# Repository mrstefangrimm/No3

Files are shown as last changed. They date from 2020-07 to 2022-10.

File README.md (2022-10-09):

# Lung Motion X-Ray Imaging Phantom
No3 (working title) is a motion phantom with 3 motion axes which are controlled independently for both linear and rotary motion.

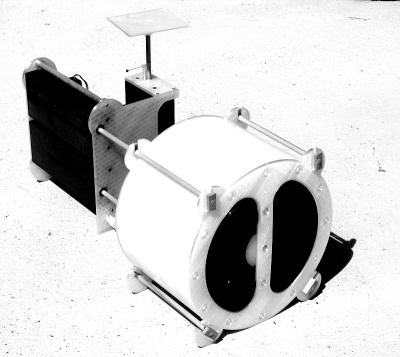
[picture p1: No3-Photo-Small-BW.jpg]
No3 Motion Phantom


A [video on youtube](https://youtu.be/cEjuUass-fE) shows how the phantom works.

## Project History
The project was realized in 2020.

## Construction

A detailed description how to build this phantom was published on *instructables.com* but removed because of a possible copyright infringement.

## Manufacturing Tool Chain

Software | License 
---- | -------
SketchUp | SketchUp Shop 
Ultimaker Cura | GPL

## License


This work is licensed under the Creative Commons Attribution-ShareAlike 4.0 International License. To view a copy of this license, visit http://creativecommons.org/licenses/by-sa/4.0/ or send a letter to Creative Commons, PO Box 1866, Mountain View, CA 94042, USA.

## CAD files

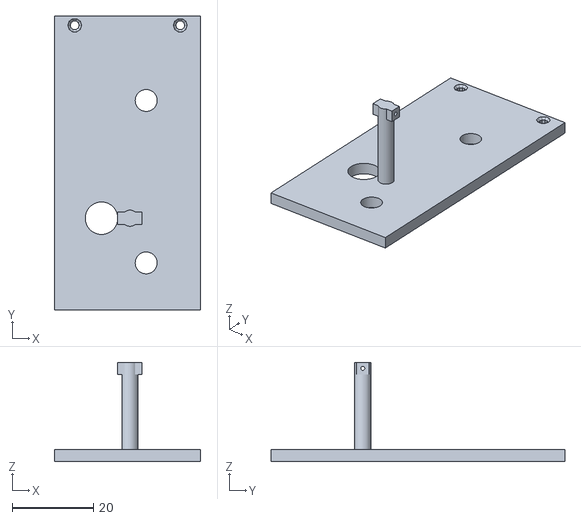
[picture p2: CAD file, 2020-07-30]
MechanicalDesign/Sketchup/Export/No3-GatingTopLeft.stl
36.0 x 72.4 x 24.5

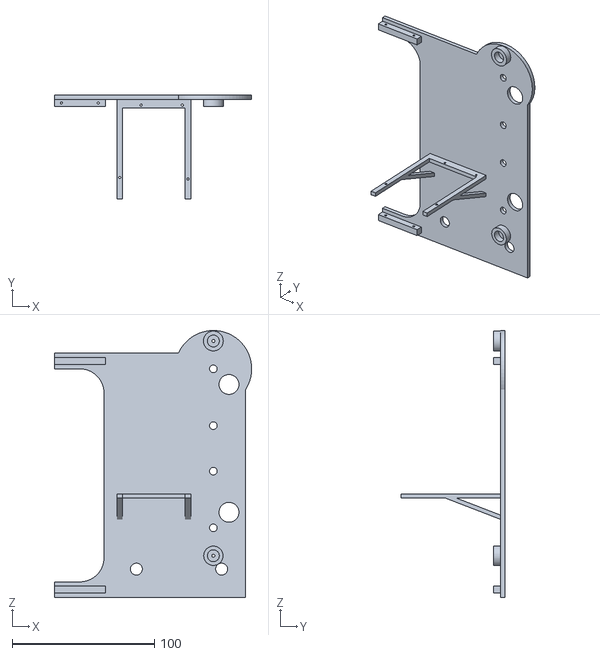
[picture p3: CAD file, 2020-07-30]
MechanicalDesign/Sketchup/Export/No3-Front.stl
139.0 x 73.0 x 188.0

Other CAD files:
MechanicalDesign/Sketchup/No3-Back.skp
MechanicalDesign/Sketchup/No3-CPUDistanceRing.skp
MechanicalDesign/Sketchup/No3-ChestBackPanel.skp
MechanicalDesign/Sketchup/No3-ChestForm.skp
MechanicalDesign/Sketchup/No3-ChestFormCover.skp
MechanicalDesign/Sketchup/No3-ChestFrontPanel.skp
MechanicalDesign/Sketchup/No3-ChestPositive.skp
MechanicalDesign/Sketchup/No3-Front.skp
MechanicalDesign/Sketchup/No3-GatingBottom.skp
MechanicalDesign/Sketchup/No3-GatingTop.skp
MechanicalDesign/Sketchup/No3-GatingTopLeft.skp
MechanicalDesign/Sketchup/No3-LungLeft.skp
MechanicalDesign/Sketchup/No3-LungLeftInsert.skp
MechanicalDesign/Sketchup/No3-LungLeftLowerCylinder.skp
MechanicalDesign/Sketchup/No3-LungLeftLowerCylinderInsert.skp
MechanicalDesign/Sketchup/No3-LungLeftUpperCylinder.skp
MechanicalDesign/Sketchup/No3-LungLeftUpperCylinderInsert.skp
MechanicalDesign/Sketchup/No3-LungRight.skp
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

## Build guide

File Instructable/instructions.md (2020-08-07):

# Lung Motion X-Ray Imaging Phantom

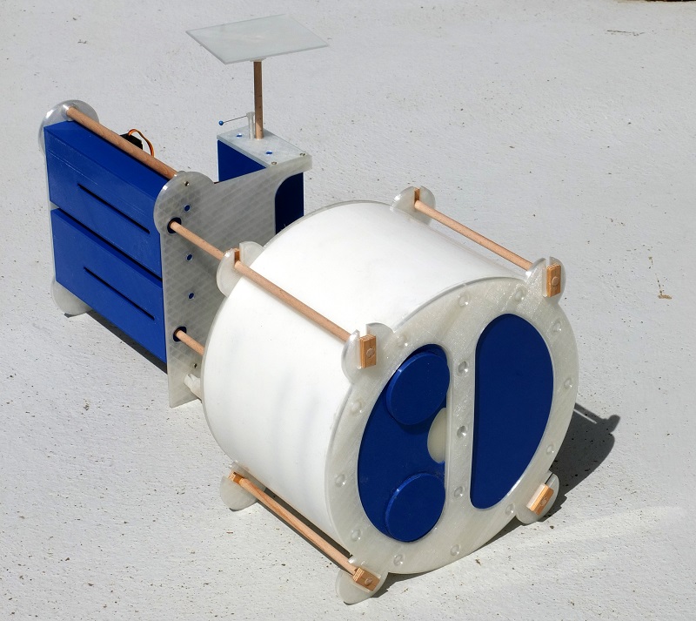
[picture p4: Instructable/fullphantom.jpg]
fullphantom


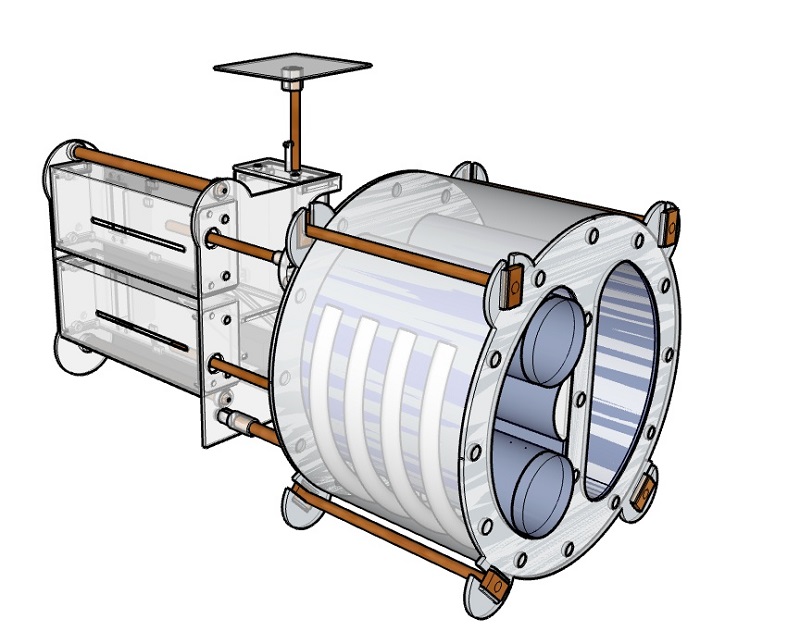
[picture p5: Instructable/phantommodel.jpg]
phantommodel


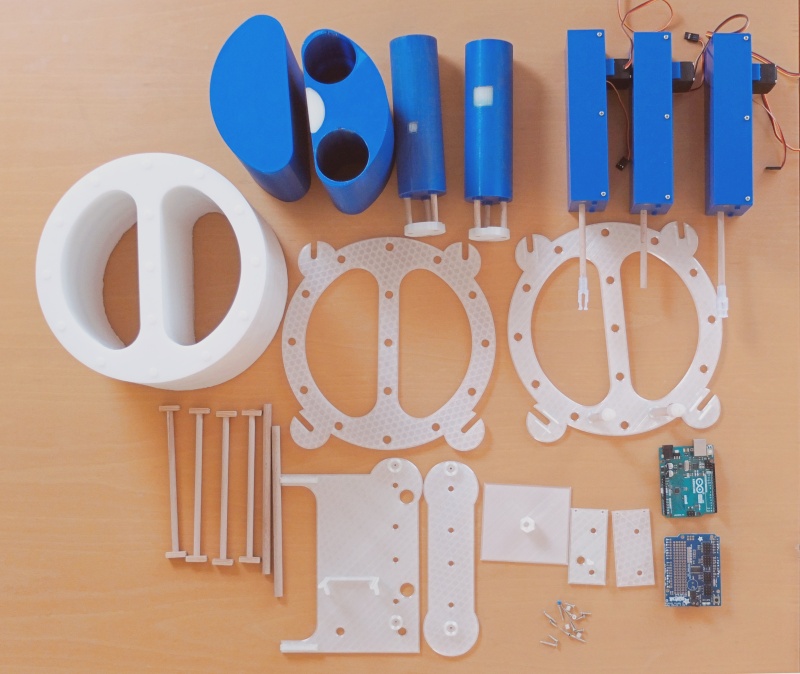
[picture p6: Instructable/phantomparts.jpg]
phantomparts


In the field of medical imaging, so called imaging phantoms are used  to evaluate, analyze, and tune the performance of various imaging  devices (Source: Wikipedia). This specially developed imaging  phantom simulates motion and deformation of a lung based on respiratory motion.

The idea for this phantom came when I studied breathing motion in a lung. The motion in the lung is not uniform. The lower part of the lung moves more sideways whereas the upper part of the lung moves up and down. To simulate this, a phantom is required that does not only simulate motion but also simulates deformation. One example that illustrates the motion in the lung: https://www.youtube.com/watch?v=kfcbAyLJHsI

On an X-Ray image, the material and the density define what is a  bone, a liver or a lung. Silicone for example is similar to human tissue whereas modelling plaster is similar to bone. The chest of this phantom is made of silicone, the cast-in rips are made of modelling plaster and the lungs are made of 3D printed PLA.

In the left lung,  there are two freely movable cylinders to simulate motion and deformation in the lung. In each cylinder there is a pocket and an object with a higher density than the density of the lung.

This short animation gives you an idea how this phantom would look like on X-Ray images. The two red arrows mark the two freely movable targets: https://youtu.be/TincNP1mlLw

To generate the motion, the phantom uses three [LnR-Actuators](https://www.instructables.com/id/Linear-and-Rotation-Actuator/), an Arduino micro controller and an Adafruit Servo Shield. The micro controller is  required because you cannot be in the room when you acquire X-Ray  images. The phantom can be either be remote controlled from a PC over an USB cable, or you can start one of the pre-programmed motion patterns and use the phantom stand-alone.

This phantom is suitable to evaluate and tune the performance of medical devices. A field of application could be the development of motion tracking and 4D reconstruction algorithms. With the used materials, imaging dosimetry should also be possible. 

The direct material costs are approximately USD 350.

### Supplies:

1 Arduino Uno

1 Adafruit 16-Channel Servo Shield

3 [LnR-Actuator](https://www.instructables.com/id/Linear-and-Rotation-Actuator/)

9 Screw M2 x l10

4 Screw M2 x l20

6 Wooden dowel d6 x l40 mm

4 Wooden dowel d6 x l150 mm

2 Wooden dowel d8 x l166 mm

2 Wooden dowel d8 x l120 mm

8 Wooden rectangular profile w10 x l20 x h4 mm with a hole d6 mm

1 Windows PC with Java 8 runtime and .NET Framework 4.6.2

1 3D Printer

1 Standing drill is of avail

750g PLA filament

750g PVA filament

3 kg of casting silicone

500g of modelling plaster

Legend: l:length, d:diameter, w: width, h:heigth

## Step 1: 3D Printed Parts

- PLA default, 20% infill: LMXIP-Back.stl, LMXIP-ChestBackPanel.stl, LMXIP-ChestFrontPanel.stl, LMXIP-CPUDistanceRing.stl, LMXIP-Front.stl, LMXIP-GatingBottom.stl, LMXIP-GatingTop.stl, Cmn-FrontClip.stl, Cmn-Flange.stl, Cmn-FlangeClip.stl, Cmn-GatingPlatform.stl

- PLA target, 90% infill: LMXIP-LungLeftInsert.stl, LungLeftLowerCylinderInsert.stl, LMXIP-LungLeftUpperCylinderInsert.stl

- PLA lung, 10% infill: LMXIP-LungLeft.stl, LMXIP-LungLeftLowerCylinder.stl, LMXIP-, LMXIP-LungLeftUpperCylinder.stl, LMXIP-LungRight.stl

- PVA form, 20% infill: LMXIP-ChestFormCover.stl, LMXIP-RipsForm.stl, LMXIP-SpineElementForm.stl, LMXIP-ChestForm.stl

## Step 2: Build the Skeleton

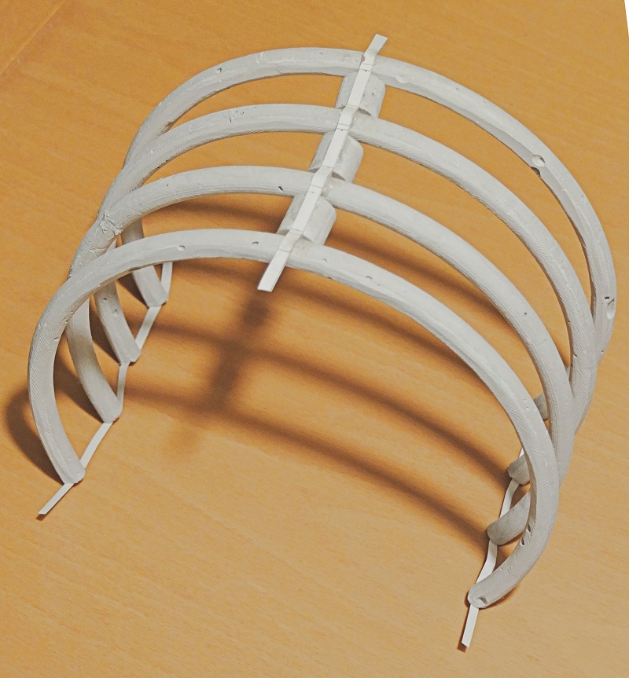
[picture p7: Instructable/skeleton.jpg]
skeleton


Mix some modeling plaster and fill the printed forms *LMXIP-RipsForm* and *LMXIP-SpineElementForm*. Wait until the plaster has dried; one day at least. Then wash off the PVA form. The plaster will not dissolve.

Use three small paper strips and glue the elements together. This is needed to insert the skeleton into the chest form.

## Step 3: Build the Phantom Body

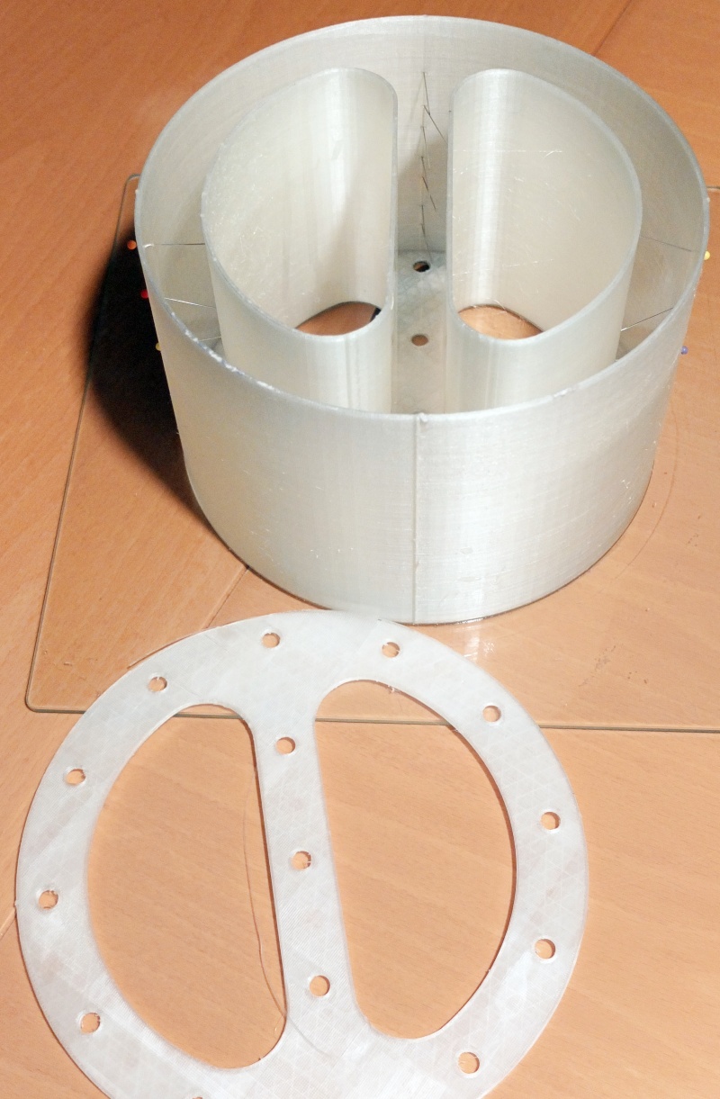
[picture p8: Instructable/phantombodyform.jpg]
phantombodyform


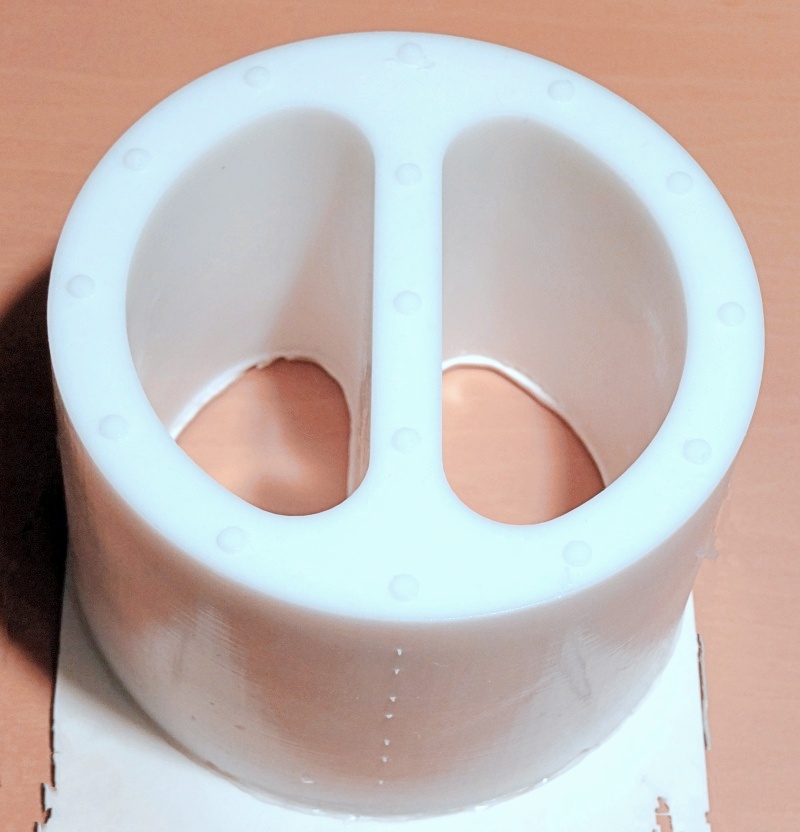
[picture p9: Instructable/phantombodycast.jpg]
phantombodycast


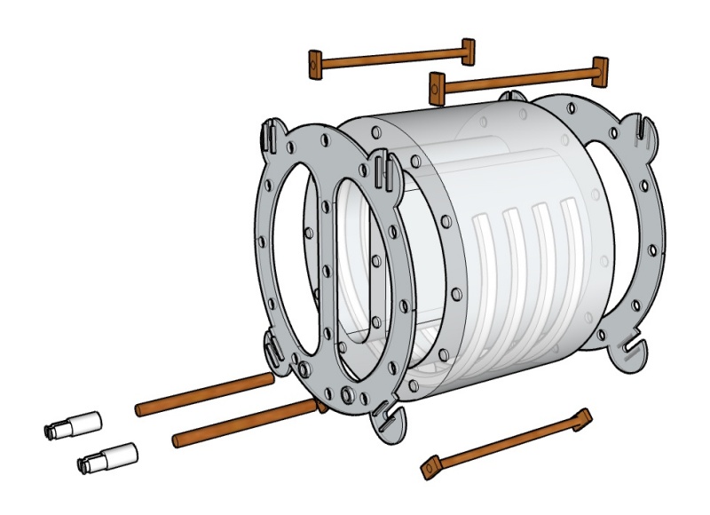
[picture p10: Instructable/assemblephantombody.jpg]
assemblephantombody


Insert the skeleton into the *LMXIP-ChestForm*. Use some pins as shown on the picture to hold the skeleton in place.

Mix the casting silicone and gentle cast it into the form. Add the *LMXIP-ChestFormCover* and wait until the silicone has hardened (read the data sheet from the manufacturer). Then wash off the PVA form.

Glue the handles (rectangular profile w10 x l20 x h4 mm) to the wooden dowels d6 x l150 mm.

Fixate the *LMXIP-ChestFrontPanel* and the *LMXIP-ChestBackPanel* with the created handles.

Insert two wooden dowels d8 x l110 mm into the holes in the front panel and attach a *Cmn-FrontClip.*

## Step 4: Add the Lungs

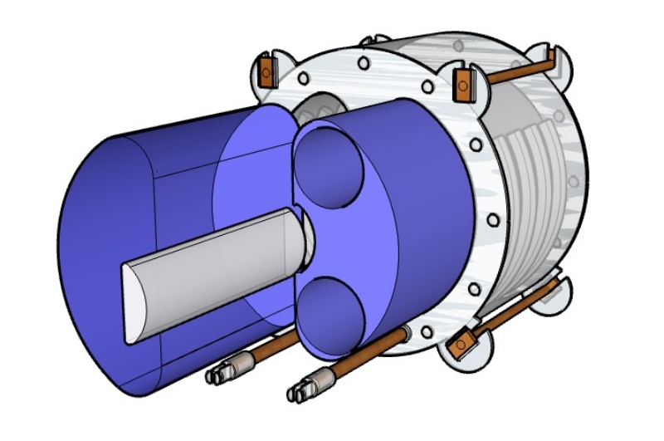
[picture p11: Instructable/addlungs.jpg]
addlungs


Glue the *LMXIP-LungLeftInsert* to the *LMXIP-LungLeft*. Gently push the *LMXIP-LungLeft* and the *LMXIP-LungRight* into the phantom.

## Step 5: Assemble the two Cylinders

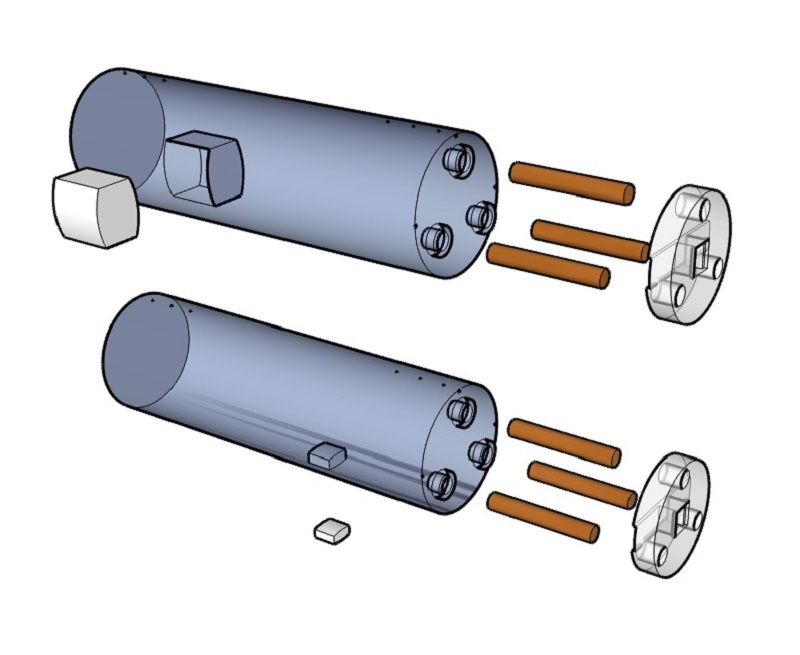
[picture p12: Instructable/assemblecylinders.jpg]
assemblecylinders


Insert the *LMXIP-LungLeftUpperCylinderInsert* into the *LMXIP-LungLeftUpperCylinder* and fixate it with a drop of glue. Insert three wooden dowels d6 x l40 mm into the holes in the front plane of the cylinder and attach a *Cmn-Flange*.

Insert the *LungLeftLowerCylinderInsert* into the *LMXIP-LungLeftLowerCylinder* and fixate it with a drop of glue. Insert three wooden  dowels d6 x l40 mm into the holes in the front plane of the cylinder and attach a *Cmn-Flange*.

## Step 6: Assemble the Actuator

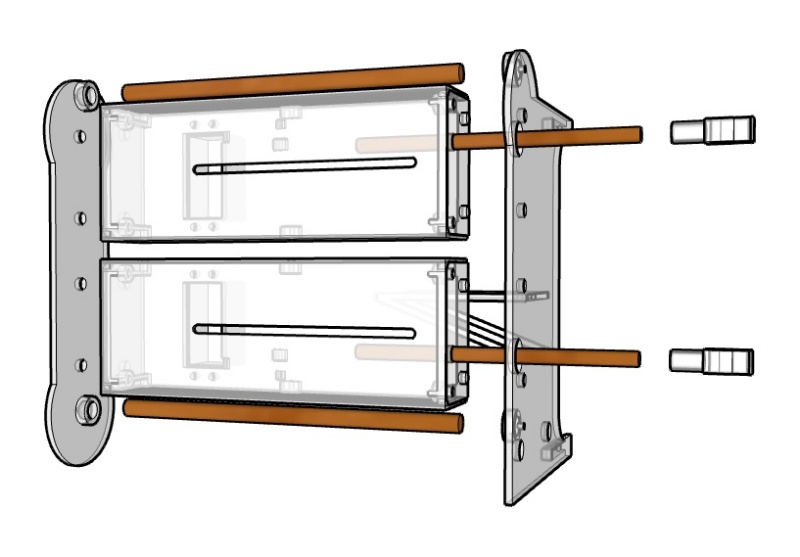
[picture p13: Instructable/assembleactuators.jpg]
assembleactuators


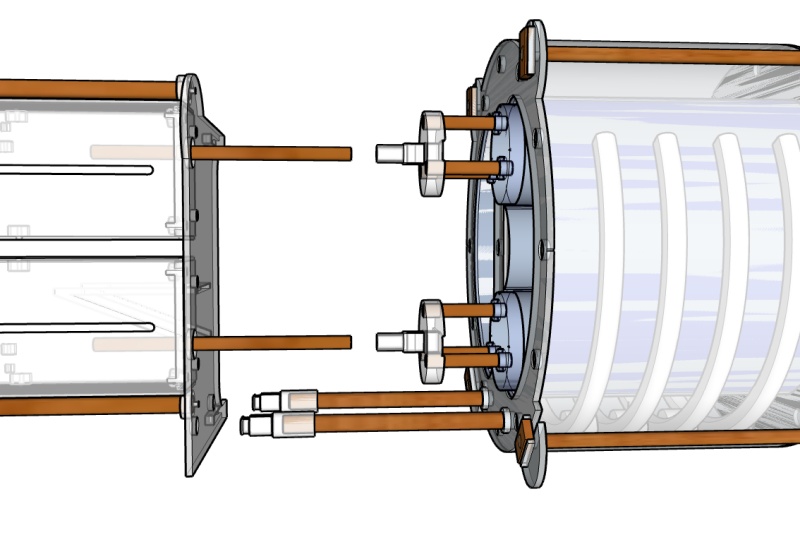
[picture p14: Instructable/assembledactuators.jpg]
assembledactuators


To build the actuator assembly, fixate two wooden dowels d8 x l166 mm to the *LMXIP-Back* with two screws M2 x l20 mm. Plug-in the two LnR-Actuators and add the *LMXIP-Front*. Add a *Cmn-FlangeClip* to each of the LnR-Actuator shafts but do not fixate it yet.

Plug-in the assembled phantom body into the actuator assembly. Connect the  flange-clip with the flange. Align the cylinders and then fixate the flange clips with some glue to the actuator shafts.

## Step 7: Add the Gating Platform

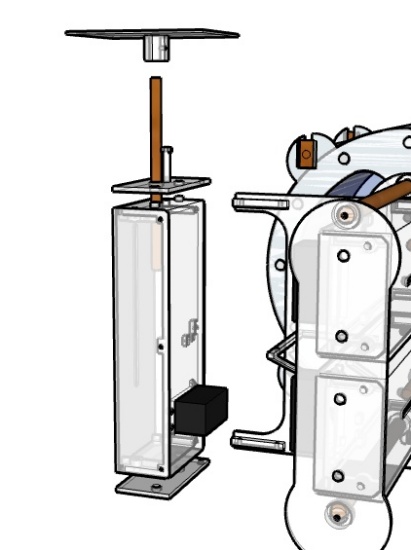
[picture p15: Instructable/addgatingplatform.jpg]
addgatingplatform


To build the Gating assembly, attach the *LMXIP-GatingBottom* to the *LMXIP-Front* with two screws M2 x l10 mm. Plug-in the LnR-Actuator and add the *LMXIP-GatingTop*. Fixate it with two screws M2x l10. Add the *Cmn-GatingPlatform* and fixate it with a screw M2 x l10 mm.

## Step 8:  Add the Micro Controller

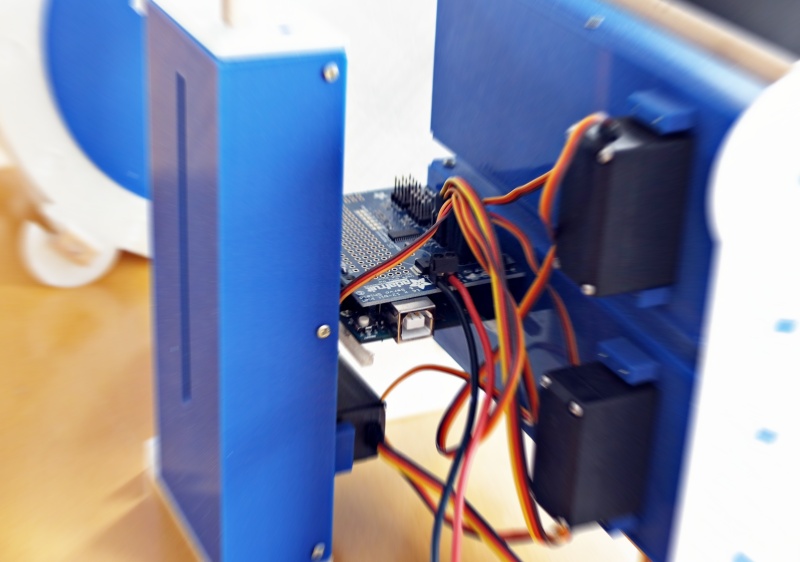
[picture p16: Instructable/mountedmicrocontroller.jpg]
mountedmicrocontroller


Use four *LMXIP-CPUDistanceRing* to mount the Arduino on the front panel and fixate it with  four screws M2 x l10 mm. Attach the Adafruit Servo Shield.

Connect the servos to the servo  shield in this order: Rotary (short cable) Lower, Upper, Gating. Longitudinal (long cable) Lower, Upper, Gating.

## Step 9: Install the Firmware and Calibrate

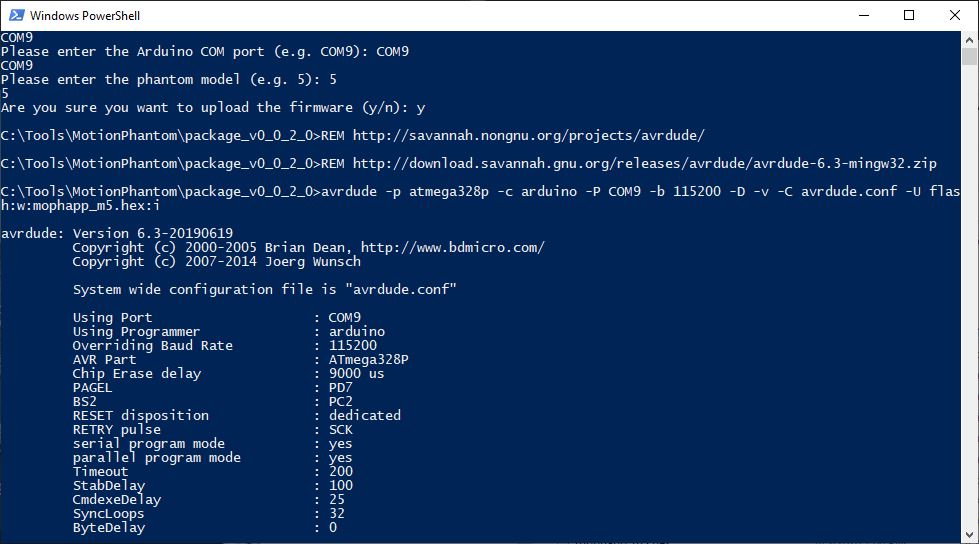
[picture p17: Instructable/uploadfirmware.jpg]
uploadfirmware


Download the package.zip (e.g. package_v0.0.2.0.zip) of the latest release from [github](https://github.com/mrstefangrimm/Phaso/releases/). The download includes the required scripts and the software to control the phantom. Unzip the package into a local folder, e.g. C:\Tools\MotionPhantom. 

Connect the phantom to your PC before the next steps.

In the download is a PowerShell script that uploads the firmware and write the calibration data to the EEPROM. To execute the script, open a PowerShell and change the directory to the target folder and then type in: .\setup.ps1 and hit <Enter>. Or right-click on the setup.ps1 and select Run with PowerShell.

- The script now lists one or more COM ports. Enter the phantom's port (e.g. COM9).

- For the model, enter: 5

- Confirm the firmware upload with: y

  The script uses avrdude to upload the firmware. After the upload, the firmware is active.

- Confirm the EEPROM update with: y

  The script writes the default calibration to the EEPROM.

- Confirm to run a test with: y

  The test ends with the output: Complete, and resets the firmware.

The phantom is ready for use.

## Step 10: Remote Control It With the Virtual Phantom Application

https://youtu.be/cEjuUass-fE

The Virtual Phantom Application is a .NET based application and part of the downloaded package (\Virms.NET\ViphApp.exe). The application simulates X-Ray imaging. And it is possible to connect and control a phantom with the application.

The program always starts with the simulation of the Marker Motion  Phantom. Change the phantom on the left control panel to "Lung Phantom".

If the phantom is plugged-in, its port should in the list. Select the port and press "Connect".

On the right control panel, it is possible to either control the motion axes individually or start a program.

If you plan to write your on software: This programming interface is completely documented in this [Wiki](https://github.com/mrstefangrimm/Phaso/wiki).

## Step 11: Control It From Your Phone

https://youtu.be/n-w-kHo6lzI

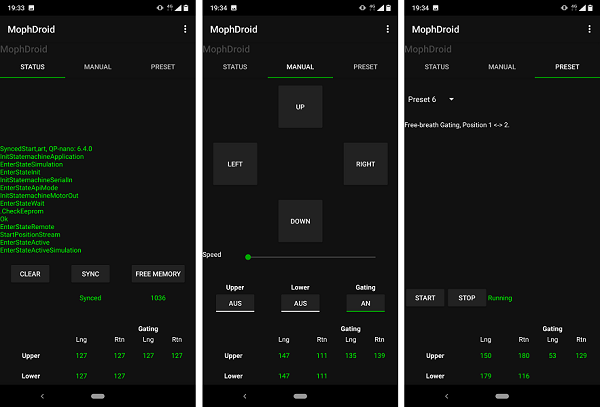
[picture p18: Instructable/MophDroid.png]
mophdroid


installmophdroid

MophDroid is a Android App that allows you to control the phantom from your phone. This App replaces the need to every time wire your PC to the phantom. Instead you may install the App on a discarded smartphone which you then leave connected to the phantom. Like this, the phantom is always ready for use.

To install the App you have to enable the developer options on your phone. Follow [these instructions](https://www.xda-developers.com/install-adb-windows-macos-linux/) to setup your phone and your PC.

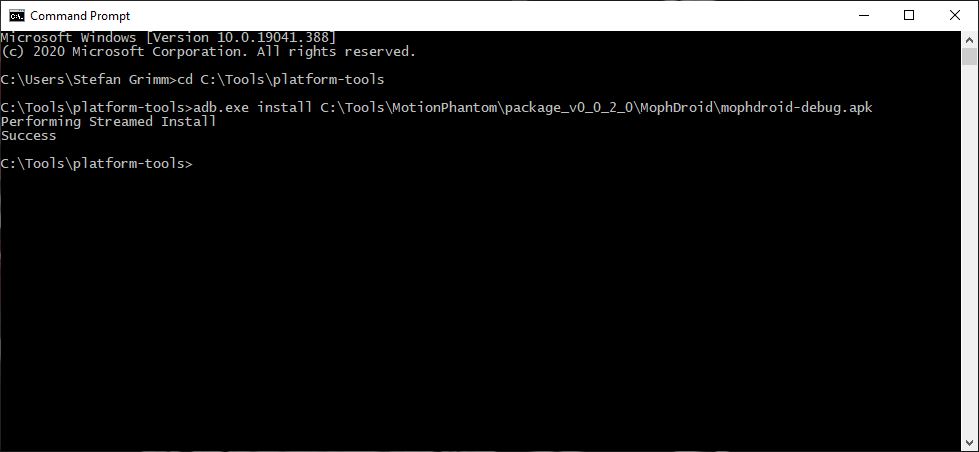
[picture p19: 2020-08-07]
Instructable/installmophdroid.jpg

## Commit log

2020-04-26 Initial check-in
    [No3-LungLeft.skp, No3-LungLeftInsert.skp, No3-LungLeftLowerCylinder.skp, No3-LungLeftLowerCylinderInsert.skp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]
2020-05-18 Update Sketchup models
    [No3-Back.skp, No3-CPUDistanceRing.skp, No3-Front.skp, No3-GatingBottom.skp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]
2020-07-30 Update instructions and add missing sketchup models
    [No3-Front.stl, No3-GatingTopLeft.stl]
2020-08-01 Rename Sketchup models.
    [No3-ChestBackPanel.skp, No3-ChestFrontPanel.skp]
2021-12-21 Rotate skeleton 180 deg.
    [No3-Skeleton.skp]
2024-02-10 Reverts Rotate skeleton by 180 deg
    [No3-Skeleton.skp]
